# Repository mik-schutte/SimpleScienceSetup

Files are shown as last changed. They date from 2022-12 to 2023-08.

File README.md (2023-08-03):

# SimpleScienceSetup
Scientific research requires a specific environment that is fine-tuned for each experiment and experimenter. Such an enviroment is referred to as a setup. To achieve the necessary specificity of a setup many parts have to be tried, tested and often replaced. However, the costs of building a setup can quickly rise and ordering/delivery can be time-consumable. Therefore, we have created a set of 3D printable assecoires that can be utilized for building your setup.

This [open-source hardware](https://hackmd.io/k3uEA4e_SAG1fw5R7pmGMQ) project is designed aims to create a starter kit for composing experimental setups. These can in turn be utilized for all kinds of purposes (e.g. education, prototyping, low-cost alternative). If you come up with new ideas for the kit we encurage you to contribute and share them on [our GitHub](https://github.com/open-make).



## Description of components
Some of the components needed to build the SimpleScienceSetup can be 3D printed or laser-cut. We provide files for:
* Breadboard
* Rod-connector at 90 degrees
* Rod-connector at flexible degrees
* Small rodent holder
* Basler camera holder

If necessary you can order any additional components such as optical posts, mounts, rails or enclosures. 

|Component|Description|
|--------|--------|
|Breadboard| A semi-portable base plate to build your setup on. Filled with 6mm mounting holes for attaching your components.|
|Rod-connector [90d]| A one-part connector that allows for the attachment of two rods at a 90-degree angle.|
|Rod-connector flex| A two-part connector that allows for the attachement of two rods at all angles.|
|Small rodent holder| A movement restricting tube that can be mounted to the broadboad.
|Basler camera holder | An attachment for connecting a Basler camera to a rod.|

## State of the Project
The project is in the research phase. As of 21-11-2022 the research involves developing of the 3D printable components. This development process is done in colaboration with the [OpenHardware Academy of the TU Delft](https://www.openhardware.academy/01_Welcome.html). In the future we aim to expand the variety of components. 

## Prototypes
In case you are wondering how each component came to be, we provide detailed design progress. This will take you through the design history and reasoning behind decisions of each accessoire. This information can be found within the folder of each component.

## Alternatives
This project serves as a low-cost alternative to distributors of optic system building blocks such as: Thorlabs and Edmundoptics. However, the higher costs of these distributors are accompanied by more solid and less breakable components. 

## License 
SimpleScienceSetup © 2023 by Mik Schutte is licensed under [CERN-OHL-S](https://ohwr.org/cern_ohl_s_v2.txt)

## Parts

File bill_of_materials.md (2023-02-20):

# SSS Bill of Materials

|Part description|Quantity|Cost|Source|
|-----|-----|-----|-----|
|Headbar holder |1 |€2,03 |3D printable file available|
|Rodent holder |1 |€5,05 |3D printable file available|
|Optical breadboard|1 |€4,56 | design file available or https://www.thorlabs.de/navigation.cfm?guide_id=40| 
|Basler camera holder|1 |€5,05 |3D printable file available|
|Basler camera with lense (optional)|1 |€319|https://www.baslerweb.com/en/products/cameras/area-scan-cameras/ace2/a2a1920-51gmbas/ |
|Rodconnector90d|1 |€3,18 |3D printable file available|
|12mm rod|2 |~€30 |https://www.thorlabs.de/newgrouppage9.cfm?objectgroup_id=1266 |
|6mm hexbolt|9 |€4,95 | https://www.amazon.de/-/en/Hexagonal-screw-full-thread-set/dp/B079DWMKKF?th=1|
|6mm hexnut|3 |€1,83 | https://www.amazon.de/Quality-Stainless-Steel-Screws-Threaded/dp/B07Q6Z9HG4/ref=sr_1_1_sspa?crid=1PRSIH5OFZF3Z&keywords=6%C2%A0mm+sechskantmutter&qid=1676921729&s=industrial&sprefix=6mm+hexnut%2Cindustrial%2C189&sr=1-1-spons&sp_csd=d2lkZ2V0TmFtZT1zcF9hdGY&psc=1|
|4mm screw|3 |€0,12|https://www.amazon.de/s?k=4mm+screw&i=industrial&crid=2SG8K2XQYQF7G&sprefix=4mm+screw%2Cindustrial%2C155&ref=nb_sb_noss_2 |
|4mm nut|3 |€0,14 | https://www.amazon.de/s?k=4mm+hexnut&i=industrial&crid=1QURA9RF97XUR&sprefix=4mm+hexnut%2Cindustrial%2C241&ref=nb_sb_noss|
|2mm screw|1 |€0,04 |https://www.amazon.de/s?k=4mm+screw&i=industrial&crid=2SG8K2XQYQF7G&sprefix=4mm+screw%2Cindustrial%2C155&ref=nb_sb_noss_2 |
|**TOTAL COST** | | |**€375,95**| |

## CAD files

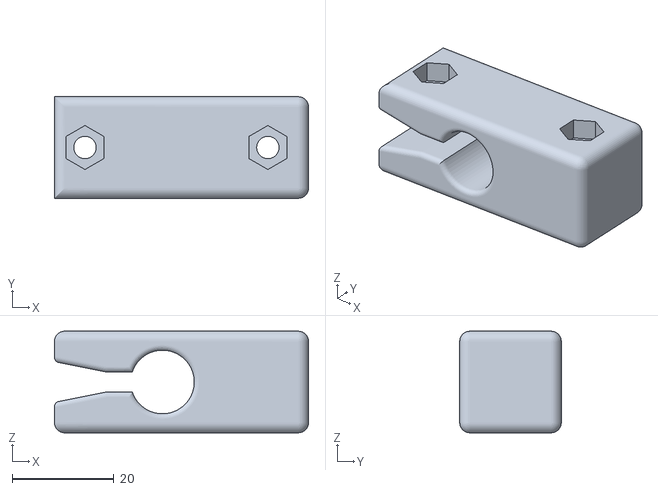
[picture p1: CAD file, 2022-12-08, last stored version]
fabrication/designs/rodconnector.stl
50.0 x 20.0 x 20.0

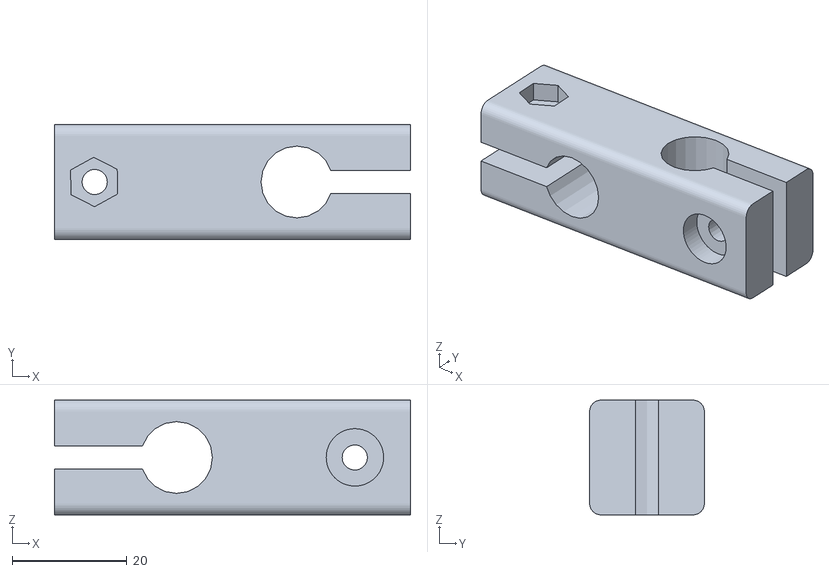
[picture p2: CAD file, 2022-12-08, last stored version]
fabrication/designs/rod_connector90d v1.stl
62.0 x 20.0 x 20.0

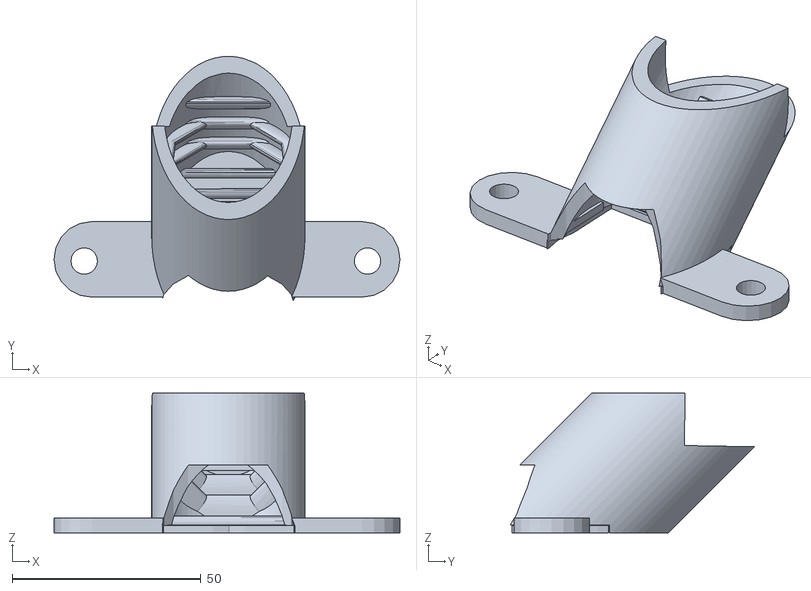
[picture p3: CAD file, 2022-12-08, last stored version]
fabrication/designs/mouse_holder.stl
91.6 x 64.7 x 37.0

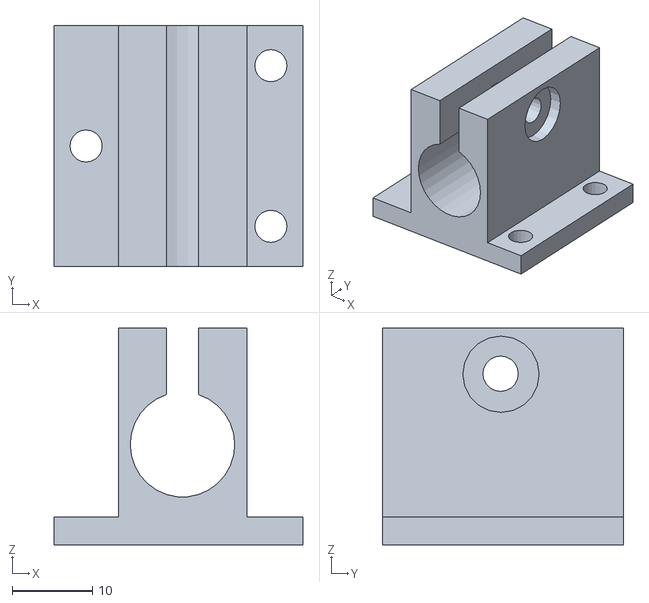
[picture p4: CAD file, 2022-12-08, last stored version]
fabrication/designs/baslercamera_holder v1.stl
31.0 x 30.0 x 27.0

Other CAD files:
fabrication/designs/rod_connector.stl

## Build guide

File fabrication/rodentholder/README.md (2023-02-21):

# Rodentholder
Headbar holder (left) and rodent holder (right) 3D-printable files for mice. 



## Details headbar holder
|Description|Value|
|---|---|
|Material| PLA
|Used filament| 9.67g
|Nozzle size| 0.4mm
|Laminar thickness| 0.2mm
|Infill| 20%
|Time to print| 01:00

## Details rodent holder
|Description|Value|
|---|---|
|Material| PLA
|Used filament| 20.2g
|Nozzle size| 0.4mm
|Laminar thickness| 0.2mm
|Infill| 20%
|Time to print| 02:11

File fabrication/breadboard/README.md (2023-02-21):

# Breadboard
Laser-cuttable optical breadboard, used as a baseplate for building the SimpleScienceSetup.



## Current status
Initialized

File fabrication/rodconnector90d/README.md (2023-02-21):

# Rodconnector 90D
3D-printable file that allows for the connecting of two rods at a 90 degree angle. Suitable rod diameter is 12mm.



# Details
|Description|Value|
|---|---|
|Material| PLA
|Used filament| 12.7g
|Nozzle size| 0.4mm
|Laminar thickness| 0.2mm
|Infill| 20%
|Time to print| 01:20

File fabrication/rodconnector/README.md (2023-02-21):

# Rodconnector
3D printable file for connecting two rods at a flexible angle. As of 20-02-2023 these can only connect 12mm rods.



## Details
|Description|Value|
|---|---|
|Material| PLA
|Used filament| 7.3g
|Nozzle size| 0.4mm
|Laminar thickness| 0.2mm
|Infill| 20%
|Time to print| 00:53

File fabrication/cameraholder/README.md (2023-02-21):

# Cameraholder
This is a 3D-printable component for fastening the Baslercamera to a rod. Currently, the only size available is for rods with a 12mm diameter.



## Details
|Description|Value|
|---|---|
|Material| PLA
|Used filament| 8.1g
|Nozzle size| 0.4mm
|Laminar thickness| 0.2mm
|Infill| 20%
|Time to print| 00:54

## Notes
Connect with 2mm screws to the camera and tichten with 4mm hexbolt and screw.

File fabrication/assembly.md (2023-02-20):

# Assembly instructions
Here we provide a comprehensive step-by-step guide on how to build an exemplary experimental setup using the components within the SimpleScienceSetup. 



## Tools required
* 6mm Tapping drill 
* Screwdriver 
* 6mm Hex key
* Level


## Material required
* Optical breadboard 
* Rod-connector 90d
* Small rodent holder
* Basler camera holder
* Basler camera with lense (optional)
* 12mm Thorlabs rod [x2]
* 6mm hexbolt [x9]
* 6mm hexnut [x3]
* 4mm screw
* 4mm nut
* 2mm screw



## Scematic
TODO: Add a scematic for the layout of the mock setup.

## Instructions
1. For each of the holes in the laser-cut breadboard tap a 6mm wire into it with a 6mm tapping drill.
2. Screw a 6mm hexbolt into each corner of the breadboard.



3. Level the breadboard by adjusting the height of each hexbolt. Use a leveler to track progess.
4. Place the small rodent holder and fasten it using two 6mm hexbolts. 



6. If your rod needs a screw to be screwed in to. Use a 6mm hesxbolt and screw it through the bottom of the optical breadboard. Note that you keep the distance and angle of your camera in mind.
7. Attach the rod to the screw.



8. Slide the hole of the rod connector 90d over the shaft of the rod. Note that a second bar will be placed at 90degrees from the original rod.
9. Clamp the rod connector 90d by holding the hexbolt in place, while fastening in the screw.



10. Place the camera holder on the bottom of the Basler camera and make sure that the hole align.
11. Screw the 2mm screws through the holes of the camera holder and into the camera holes to fasten the camera to the camera holder.



12. Connect the second rod with the rod connector 90d and fasten it conform step 9-10.
13. Slide the camera holder over the rod.



---
Congratulations you have completed assembling your own SimpleScienceSetup! :thumbsup: :confetti_ball: :balloon:

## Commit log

2023-01-24 Created assembly.md
    Provide the file explaining how to build
2023-01-24 update details.md
    added print details
2023-02-21 reorder frames
